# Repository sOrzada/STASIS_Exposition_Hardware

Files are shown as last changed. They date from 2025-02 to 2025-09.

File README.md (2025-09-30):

# STASIS_Exposure_Hardware
This is the repository for the exposure hardware of the STASIS project.
The corresponding software can be found in this repository: https://github.com/sOrzada/STASIS_Control

by Stephan Orzada @ German Cancer Research Center (DKFZ) 

# Overview
The STASIS RF exposure system is an open-source hardware and software platform designed for implant testing under exposure to radiofrequency (RF) fields, such as those encountered in the environment of an MRI system. For this purpose, the target RF frequency is 128 MHz, corresponding to the resonant frequency of protons in a 3 Tesla magnetic field. The system is capable of transmitting on eight independent RF channels, enabling parallel transmission.
To ensure the design is easily accessible to potential users, all design files and software are publicly available and can be accessed via the following repositories:
https://github.com/sOrzada/STASIS_Exposure_Hardware
https://github.com/sOrzada/STASIS_Control
All hardware components of the exposure system are licensed under the CERN-OHL-W while the software is licensed under a GNU GPL v3. In addition the project has been submitted to the conformity assessment body of the Open Source Imaging Initiative e.V. (https://www.opensourceimaging.org) to assess its open source status according to DIN SPEC 3105.  
To further improve accessibility, standard components with long production lifespans were selected wherever possible. For example, standard logic components were used instead of specialised microcontrollers or FPGAs.

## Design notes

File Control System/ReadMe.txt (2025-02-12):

This Folder contains the PCBs and Housings for the Control System of the STASIS project's RF exposition system.
The PCBs are provided in two different formats: Eagle and KiCAD.
The Housings-folder contains .step files for the housings and front panels of the Eurocards.

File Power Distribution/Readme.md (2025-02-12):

# Power Distribution
This folder contains the data for the power distribution of the STASIS RF exposition system.
The Power Distribution is provides a simple switch (and emergency switch) to switch the system's power on and off.
Furthermore, it switches each amplifier on 3s after the previous amplifier to prevent circuit breakers from acting.

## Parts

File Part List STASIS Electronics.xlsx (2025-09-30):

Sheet: Components Control System
Article | Description | URL | Amount | Unit Price | Subtotal | Distributor | Comment | Total
9031646921 | DIN41612 64P Typ C Male | 9031646921 (https://www.mouser.de/ProductDetail/HARTING/09031646921?qs=gIpPgrDBK%2Fgxgy%2FzqITWPQ%3D%3D) | 20 | 2.88 € | 57.60 € | Mouser | Modulators | 3439.22 €
9032646825 | DIN41612 64P Typ C Female | 9032646825 (https://www.mouser.de/ProductDetail/HARTING/09032646825?qs=gIpPgrDBK%2Fibxr4BbAh3hw%3D%3D) | 20 | 2.70 € | 54.00 € | Mouser
GCM188R71C104KA37J | 100nF 0603 | GCM188R71C104KA37J (https://www.mouser.de/ProductDetail/Murata-Electronics/GCM188R71C104KA37J?qs=sGAEpiMZZMvsSlwiRhF8qqDvUs8Zl92XYFoMhbKeCr4%3D) | 500 | 0.03 € | 13.50 € | Mouser
GRM1885C1H111GA01J | 110pF 0603 | GRM1885C1H111GA01J (https://www.mouser.de/ProductDetail/Murata-Electronics/GRM1885C1H111GA01J) | 30 | 0.11 € | 3.36 € | Mouser
C0603C271G2GACTU | 270pF 0603 | C0603C271G2GACTU (https://www.mouser.de/ProductDetail/KEMET/C0603C271G2GACTU) | 25 | 0.42 € | 10.50 € | Mouser
GCM1885C2A221JA16D | 220pF 0603 | GCM1885C2A221JA16D (https://www.mouser.de/ProductDetail/Murata-Electronics/GCM1885C2A221JA16D) | 25 | 0.07 € | 1.88 € | Mouser
EMF316AB7106KLHT | 10µF 1206 | EMF316AB7106KLHT (https://www.mouser.de/ProductDetail/Taiyo-Yuden/EMF316AB7106KLHT) | 50 | 0.21 € | 10.75 € | Mouser
GCM31CR70J226KE23L | 22µF 1206 | GCM31CR70J226KE23L (https://www.mouser.de/ProductDetail/Murata-Electronics/GCM31CR70J226KE23L) | 50 | 0.49 € | 24.45 € | Mouser
GRM1555C1E103JE01D | 10nF 0402 | GRM1555C1E103JE01D (https://www.mouser.de/ProductDetail/Murata-Electronics/GRM1555C1E103JE01D) | 50 | 0.08 € | 4.00 € | Mouser
08055A102KAT2A | 1nF 0805 | 08055A102KAT2A (https://www.mouser.de/ProductDetail/KYOCERA-AVX/08055A102KAT2A?qs=sGAEpiMZZMvsSlwiRhF8qsUJX4ZZq7O1iub2rREDztE%3D) | 100 | 0.16 € | 16.20 € | Mouser
GCM188R71H103KA37J | 10nF 0603 | GCM188R71H103KA37J (https://www.mouser.de/ProductDetail/Murata-Electronics/GCM188R71H103KA37J) | 500 | 0.02 € | 10.50 € | Mouser
BAT60BE6327HTSA1 | Schottky Diode SOD-323-2 | BAT60BE6327HTSA1 (https://www.mouser.de/ProductDetail/Infineon-Technologies/BAT60BE6327HTSA1?qs=K00xGehIljs1ioYh6e6mQw%3D%3D) | 30 | 0.41 € | 12.18 € | Mouser
SN74ALVC00NSR | Quad 2-Input Nand LVC SOIC-14 | https://www.mouser.de/ProductDetail/Texas-Instruments/SN74ALVC00NSR?qs=LfG3tU9ud8CLiczQYRPDsg%3D%3D | 10 | 0.44 € | 4.42 € | Mouser
SN74LVC04ANS | Hex Inverter LVC SOIC-14 | SN74LVC04ANS (https://www.mouser.de/ProductDetail/Texas-Instruments/SN74LVC04ANS?qs=4%2FQr8XCwynNuUCMn78xqww%3D%3D) | 10 | 0.99 € | 9.89 € | Mouser
SN74HC688DW | Comparator SO20W | SN74HC688DW (https://www.mouser.de/ProductDetail/Texas-Instruments/SN74HC688DW?qs=EIjG%252BN7kn%252BnsG9O57JMTyQ%3D%3D) | 50 | 1.36 € | 68.00 € | Mouser
SN74LVC1G17DCKR | Buffer single SC70-5 | SN74LVC1G17DCKR (https://www.mouser.de/ProductDetail/Texas-Instruments/SN74LVC1G17DCKR?qs=L5CvrNUdZioM7CGWSWVycQ%3D%3D) | 100 | 0.12 € | 12.00 € | Mouser
SN74LVC16373DLR | 16-bit Latch | SN74LVC16373DLR (https://www.mouser.de/ProductDetail/Texas-Instruments/SN74LVC16373DLR?qs=B7lSdIxWQklXUX7U1kIe%252BA%3D%3D) | 30 | 1.35 € | 40.50 € | Mouser
SN74LVC1G32DCKR | Single OR SC70-5 | SN74LVC1G32DCKR (https://www.mouser.de/ProductDetail/Texas-Instruments/SN74LVC1G32DCKR?qs=rshUhwi3fbYur8p35NB%252BLQ%3D%3D) | 100 | 0.16 € | 15.80 € | Mouser
SN74CB3Q16245DLR | 16bit bus switch ssop-48 | SN74CB3Q16245DLR (https://www.mouser.de/ProductDetail/Texas-Instruments/SN74CB3Q16245DLR?qs=ULgY8XwKjTnD7VhHoGZVNg%3D%3D) | 20 | 3.07 € | 61.40 € | Mouser
SN74LVCH16244ADLR | 16bit bus driver ssop-48 | SN74LVCH16244ADLR (https://www.mouser.de/ProductDetail/Texas-Instruments/SN74LVCH16244ADLR?qs=LfG3tU9ud8AVKX602AwiWw%3D%3D) | 40 | 1.41 € | 56.40 € | Mouser
SN74LVC1G04DCKR | Single Inverter SC70-5 | SN74LVC1G04DCKR (https://www.mouser.de/ProductDetail/Texas-Instruments/SN74LVC1G04DCKR?qs=dT9u2OTAaVWNPsQmeXyvkg%3D%3D) | 100 | 0.13 € | 13.40 € | Mouser
SN74LVC1G08DCKR | Single 2-Input AND SC70-5 | SN74LVC1G08DCKR (https://www.mouser.de/ProductDetail/Texas-Instruments/SN74LVC1G08DCKR?qs=sbcp%2F4gpy0%2F8FFQ%252BRQ5MTw%3D%3D) | 100 | 0.16 € | 16.40 € | Mouser
SN74LVC02ADRG4 | Quad 2-Input NOR | SN74LVC02ADRG4 (https://www.mouser.de/ProductDetail/Texas-Instruments/SN74LVC02ADRG4?qs=UG%2F8xqv%2F6WcgNHMmDPIwsw%3D%3D) | 18 | 0.39 € | 7.09 € | Mouser
10129381-904003BLF | Pin-Header 2x2 | 10129381-904003BLF (https://www.mouser.de/ProductDetail/Amphenol-FCI/10129381-904003BLF?qs=0lQeLiL1qyY7Xp84ndpsoA%3D%3D) | 16 | 0.10 € | 1.63 € | Mouser
77313-118-08LF | Pin-Header 2x4 | 77313-118-08LF (https://www.mouser.de/ProductDetail/Amphenol-FCI/77313-118-08LF?qs=xJiur%252Bgubk2jBBhypBJ8Ng%3D%3D) | 16 | 0.56 € | 8.96 € | Mouser
SX1100-B | Jumper | SX1100-B (https://www.mouser.de/ProductDetail/Kycon/SX1100-B?qs=oKK8NaWdAJvUJDIn2yWqug%3D%3D) | 100 | 0.04 € | 3.60 € | Mouser
0805AF-102XJRC | 1µH 0805 (2012) | 0805AF-102XJRC (https://www.mouser.de/ProductDetail/Coilcraft/0805AF-102XJRC?qs=JVZp5BaCFzh9pCHBndldQg%3D%3D) | 40 | 1.60 € | 64.00 € | Mouser
B82498F1152J | 1.5µH 0805 (2012) | B82498F1152J (https://www.mouser.de/ProductDetail/EPCOS-TDK/B82498F1152J?qs=iux7VCIsw52WrSZpCSeghA%3D%3D) | 40 | 0.58 € | 23.36 € | Mouser
WP710A10GD | 3mm LED Green | WP710A10GD (https://www.mouser.de/ProductDetail/Kingbright/WP710A10GD?qs=wRBQ8ZgBZ99oELJK8ikwDw%3D%3D) | 100 | 0.10 € | 10.00 € | Mouser
WP710A10ID | 3mm LED Red | WP710A10ID (https://www.mouser.de/ProductDetail/Kingbright/WP710A10ID?qs=wRBQ8ZgBZ98VyHeNIlWGkQ%3D%3D) | 100 | 0.10 € | 9.60 € | Mouser
RC0603FR-07100KL | 100kOhm 0603 | RC0603FR-07100KL (https://www.mouser.de/ProductDetail/YAGEO/RC0603FR-07100KL) | 500 | 0.01 € | 4.00 € | Mouser
RT0603BRE0750RL | 50Ohm 0603 | RT0603BRE0750RL (https://www.mouser.de/ProductDetail/YAGEO/RT0603BRE0750RL) | 100 | 0.11 € | 11.00 € | Mouser
ERJ-3EKF2001V | 2kOhm 0603 | ERJ-3EKF2001V (https://www.mouser.de/ProductDetail/Panasonic/ERJ-3EKF2001V?qs=sGAEpiMZZMvdGkrng054t8ugkoYZivkg3Db3Qcil2N0%3D) | 100 | 0.02 € | 2.00 € | Mouser
ERJ-3EKF2200V | 220Ohm 0603 | ERJ-3EKF2200V (https://www.mouser.de/ProductDetail/Panasonic/ERJ-3EKF2200V) | 100 | 0.02 € | 2.30 € | Mouser
ERJ-3GEY0R00V | 0Ohm 0603 | ERJ-3GEY0R00V (https://www.mouser.de/ProductDetail/Panasonic/ERJ-3GEY0R00V?qs=sGAEpiMZZMvdGkrng054t8ugkoYZivkg2RChYk5Dqt4%3D) | 100 | 0.02 € | 1.80 € | Mouser
ERJ-3EKF1001V | 1kOhm 0603 | ERJ-3EKF1001V (https://www.mouser.de/ProductDetail/Panasonic/ERJ-3EKF1001V?qs=sGAEpiMZZMvdGkrng054t8ugkoYZivkggtU4PdGL4Nk%3D) | 100 | 0.02 € | 2.00 € | Mouser
RC0603FR-07120RL | 120Ohm 0603 | RC0603FR-07120RL (https://www.mouser.de/ProductDetail/YAGEO/RC0603FR-07120RL) | 100 | 0.01 € | 0.70 € | Mouser
RC0603JR-13150RL | 150Ohm 0603 | RC0603JR-13150RL (https://www.mouser.de/ProductDetail/YAGEO/RC0603JR-13150RL) | 100 | 0.01 € | 0.90 € | Mouser
ADF08S04 | DIP switch 8 pos | ADF08S04 (https://www.mouser.de/ProductDetail/TE-Connectivity-Alcoswitch/ADF08S04?qs=SxaZfIVsCL01789ROZ7rzA%3D%3D) | 20 | 1.23 € | 24.60 € | Mouser
CY7C1021DV33-10ZSXIT | 64kx16 SRAM 10ns TSSOP-44II | CY7C1021DV33-10ZSXIT (https://www.mouser.de/ProductDetail/Infineon-Technologies/CY7C1021DV33-10ZSXIT?qs=PWZFpmwd5helP4DfKACbOQ%3D%3D) | 20 | 2.84 € | 56.80 € | Mouser
AD9754ARUZRL7 | 14-Bit ADC | AD9754ARUZRL7 (https://www.mouser.de/ProductDetail/Analog-Devices/AD9754ARUZRL7?qs=BpaRKvA4VqHe4d7qgcQcsg%3D%3D) | 20 | 24.95 € | 499.00 € | Mouser
DS1100LZ-20+ | 20ns Delay | DS1100LZ-20+ (https://www.mouser.de/ProductDetail/Maxim-Integrated/DS1100LZ-20%2b?qs=0Y9aZN%252BMVCV%2Fdv2VkDG0dA%3D%3D) | 10 | 8.09 € | 80.90 € | Mouser
ADL5385ACPZ-R7 | IQ-Modulator | ADL5385ACPZ-R7 (https://www.mouser.de/ProductDetail/Analog-Devices/ADL5385ACPZ-R7?qs=BpaRKvA4VqG4OwtCMETyCw%3D%3D) | 10 | 13.37 € | 133.70 € | Mouser
74LV393PW-Q100J | Counter IC | 74LV393PW-Q100J (https://www.mouser.de/ProductDetail/Nexperia/74LV393PW-Q100J?qs=fi7yB2oewZl1A%252BSGpgQ5jw%3D%3D) | 30 | 0.39 € | 11.64 € | Mouser
AZ1117IH-3.3TRG1 | LDO 3.3V | AZ1117IH-3.3TRG1 (https://www.mouser.de/ProductDetail/Diodes-Incorporated/AZ1117IH-3.3TRG1?qs=cpo3%2FpBou2jnS4SxLgAVoA%3D%3D) | 20 | 0.32 € | 6.42 € | Mouser
CONSMA002-L-G | SMA Con PCB-Panel | CONSMA002-L-G (https://www.mouser.de/ProductDetail/Linx-Technologies/CONSMA002-L-G?qs=vLWxofP3U2xfxfFnu8BdmA%3D%3D) | 50 | 5.81 € | 290.50 € | Mouser
710-860080375014 | 470µF 5mm | 860080375014 (https://www.mouser.de/ProductDetail/Wurth-Elektronik/860080375014?qs=0KOYDY2FL28YdH%252B8vgE2%252Bg%3D%3D) | 10 | 0.40 € | 4.00 € | Mouser | Power Supply
CR1206-FX-3300ELF | 330Ohm 1206 | CR1206-FX-3300ELF (https://www.mouser.de/ProductDetail/Bourns/CR1206-FX-3300ELF) | 100 | 0.02 € | 1.90 € | Mouser
HH18N102J500CT | 1nF 0603 | HH18N102J500CT (https://www.mouser.de/ProductDetail/Walsin/HH18N102J500CT) | 100 | 0.04 € | 3.50 € | Mouser | RF Splitter
B82498F3331J | 330nH 0805 | B82498F3331J (https://www.mouser.de/ProductDetail/EPCOS-TDK/B82498F3331J?qs=iux7VCIsw50bUV7hgS9AGw%3D%3D) | 10 | 0.48 € | 4.84 € | Mouser
TQP3M9008 | Broadband Amplifier | TQP3M9008 (https://www.mouser.de/ProductDetail/Qorvo/TQP3M9008?qs=ntQ%252BU8WgpwBNeAEBW36TMQ%3D%3D) | 5 | 6.07 € | 30.35 € | Mouser
GQM2195C2E180FB12D | 18pF 0805 RF capacitor | GQM2195C2E180FB12D (https://www.mouser.de/ProductDetail/Murata-Electronics/GQM2195C2E180FB12D?qs=sGAEpiMZZMvsSlwiRhF8qp0RtCwjIWiPtjVhVFjjz2I%3D) | 5 | 1.95 € | 9.75 € | Mouser | Signal Source
GQM2195C2E220JB12D | 22pF 0805 RF cap | GQM2195C2E220JB12D (https://www.mouser.de/ProductDetail/Murata-Electronics/GQM2195C2E220JB12D) | 5 | 0.92 € | 4.60 € | Mouser
GQM2195C2E330FB12D | 33pF 0805 RF cap | GQM2195C2E330FB12D (https://www.mouser.de/ProductDetail/Murata-Electronics/GQM2195C2E330FB12D) | 5 | 1.35 € | 6.75 € | Mouser
C1206C104J1RACAUTO | 100nF 1206 | C1206C104J1RACAUTO (https://www.mouser.de/ProductDetail/KEMET/C1206C104J1RACAUTO) | 100 | 0.11 € | 11.30 € | Mouser
SN74LVC1G02DCKR | Single 2-Input NOR SC70-5 | SN74LVC1G02DCKR (https://www.mouser.de/ProductDetail/Texas-Instruments/SN74LVC1G02DCKR?qs=HE9hdJajmerjAA9y3nGmcA%3D%3D) | 100 | 0.18 € | 17.60 € | Mouser
SN74LVC14ADRG3 | Hex Schmitt Inverter | SN74LVC14ADRG3 (https://www.mouser.de/ProductDetail/Texas-Instruments/SN74LVC14ADRG3?qs=C44r%252BX3hXgLOyR9T1KaQVg%3D%3D) | 5 | 0.54 € | 2.70 € | Mouser
AISC-1210-15NJ-T | 15nH 1210 | AISC-1210-15NJ-T (https://www.mouser.de/ProductDetail/ABRACON/AISC-1210-15NJ-T?qs=KpdAywxU010wlpUJrM445A%3D%3D) | 5 | 0.42 € | 2.10 € | Mouser
AISC-1210-R10J-T | 100nH 1210 | AISC-1210-R10J-T (https://www.mouser.de/ProductDetail/ABRACON/AISC-1210-R10J-T?qs=KpdAywxU011R3vUg8dJEpA%3D%3D) | 5 | 0.42 € | 2.10 € | Mouser
AISC-1210-82NJ-T | 82nH 1210 | AISC-1210-82NJ-T (https://www.mouser.de/ProductDetail/ABRACON/AISC-1210-82NJ-T?qs=KpdAywxU012iT2rq3hFlSg%3D%3D) | 5 | 0.35 € | 1.75 € | Mouser
AISC-1210-47NJ-T | 47nH 1210 | AISC-1210-47NJ-T (https://www.mouser.de/ProductDetail/ABRACON/AISC-1210-47NJ-T?qs=KpdAywxU010N9TqK2B9vCg%3D%3D) | 5 | 0.47 € | 2.35 € | Mouser
ERJ-6ENF1000V | 100Ohm 0805 | ERJ-6ENF1000V (https://www.mouser.de/ProductDetail/Panasonic/ERJ-6ENF1000V?qs=sGAEpiMZZMvdGkrng054t8ugkoYZivkgkz4QOj5IEgA%3D) | 100 | 0.02 € | 1.80 € | Mouser
RC0805FR-0768RL | 68 Ohm 0805 | RC0805FR-0768RL (https://www.mouser.de/ProductDetail/YAGEO/RC0805FR-0768RL?qs=sGAEpiMZZMvdGkrng054t8AJgcdMkx7x639rC03oyTs%3D) | 100 | 0.02 € | 1.70 € | Mouser
XLH538128.000000X | 128MHz CXO | XLH538128.000000X (https://www.mouser.de/ProductDetail/Renesas-Electronics/XLH538128.000000X?qs=itIaUkCn8qAeHGw2uhrs5w%3D%3D) | 5 | 2.38 € | 11.90 € | Mouser
MASWSS0115TR-3000 | RF switch SC70-6 | MASWSS0115TR-3000 (https://www.mouser.de/ProductDetail/MACOM/MASWSS0115TR-3000?qs=3Wmz%2FrCSAaEflvnPFG8Leg%3D%3D) | 10 | 1.42 € | 14.20 € | Mouser
SN74LV595ANSR | 8bit shift register | SN74LV595ANSR (https://www.mouser.de/ProductDetail/Texas-Instruments/SN74LV595ANSR?qs=UG%2F8xqv%2F6Wf1l209BjiXvA%3D%3D) | 10 | 1.07 € | 10.70 € | Mouser | SPI2Parallel
SN74LVC1G14DCKR | Single Schmitt Inverter | SN74LVC1G14DCKR (https://www.mouser.de/ProductDetail/Texas-Instruments/SN74LVC1G14DCKR?qs=j%2FZo4ajzVJKuhrRdLjfZIw%3D%3D) | 100 | 0.13 € | 12.80 € | Mouser
SN74LV393ANSR | Counter IC | SN74LV393ANSR (https://www.mouser.de/ProductDetail/Texas-Instruments/SN74LV393ANSR?qs=DcvZ7Fltd5w%252BshIxx2S2Bg%3D%3D) | 25 | 0.97 € | 24.27 € | Mouser
ERJ-3EKF1801V | 1.8kOhm 0603 | ERJ-3EKF1801V (https://www.mouser.de/ProductDetail/Panasonic/ERJ-3EKF1801V) | 100 | 0.02 € | 2.00 € | Mouser
CRCW0603220KFKEAC | 220KOhm 0603 | CRCW0603220KFKEAC (https://www.mouser.de/ProductDetail/Vishay-Dale/CRCW0603220KFKEAC) | 100 | 0.01 € | 0.80 € | Mouser
MM74HCT04MX | Hex Inverter HCT | MM74HCT04MX (https://www.mouser.de/ProductDetail/onsemi-Fairchild/MM74HCT04MX?qs=PYCkqoTEwR3wTRhpHjpTmg%3D%3D) | 3 | 0.69 € | 2.07 € | Mouser | UBL Splitter
ERJ-3GEYJ331V | 330Ohm 0603 | ERJ-3GEYJ331V (https://www.mouser.de/ProductDetail/Panasonic/ERJ-3GEYJ331V?qs=sGAEpiMZZMvdGkrng054t8ugkoYZivkgRPsbNS3nhOU%3D) | 100 | 0.02 € | 1.80 € | Mouser
ECS-TXO-2520MV-100-AN-TR | 10MHz TXO | ECS-TXO-2520MV-100-AN-TR (https://www.mouser.de/ProductDetail/ECS/ECS-TXO-2520MV-100-AN-TR?qs=bAKSY%2FctAC6D4eEwENGu8g%3D%3D) | 3 | 3.07 € | 9.21 € | Mouser | Timing Control
74LVC2G74DP,125 | D-Flip-Flop | 74LVC2G74DP,125 (https://www.mouser.de/ProductDetail/Nexperia/74LVC2G74DP125?qs=me8TqzrmIYX1iMHaYTXJug%3D%3D) | 5 | 0.51 € | 2.55 € | Mouser
UMFT4222EV-D | USB 2.0 to SPI Module | UMFT4222EV-D (https://www.mouser.de/ProductDetail/FTDI/UMFT4222EV-D?qs=F5EMLAvA7ICRJCgnkJGADg%3D%3D) | 2 | 20.63 € | 41.26 € | Mouser
BCS-112-L-S-TE | Sockel 12x1 | BCS-112-L-S-TE (https://www.mouser.de/ProductDetail/Samtec/BCS-112-L-S-TE?qs=92ilVni64gzptLUYzm9OlQ%3D%3D) | 4 | 3.32 € | 13.28 € | Mouser
77311-118-02LF | Pin Header 2x1 | 77311-118-02LF (https://www.mouser.de/ProductDetail/Amphenol-FCI/77311-118-02LF?qs=5xI8GKdkXlmD4cdGgiyi7w%3D%3D) | 4 | 0.24 € | 0.96 € | Mouser
AJ25HV | Trimmer 1-23pF 750V | AJ25HV (https://www.digikey.de/en/products/detail/knowles-voltronics/AJ25HV/7261406) | 20 | 48.89 € | 977.72 € | Digikey
SCA-4-10+ | 4-Way Splitter | SCA-4-10+ (https://www.minicircuits.com/WebStore/dashboard.html?model=SCA-4-10%2B) | 10 | 7.27 € | 72.70 € | Mini-Circuits
AKL 320-02 | Anschlussklemme 2-Pol Vert. | AKL 320-02 (https://www.reichelt.de/wannenstecker-fuer-akl-349-2-pol-rm5-0-akl-320-02-p36672.html?trstct=pos_9&nbc=1) | 5 | 0.33 € | 1.65 € | Reichelt
AKL 330-02 | Anschlussklemme 2-Pol Hor. | AKL 330-02 (https://www.reichelt.de/wannenstecker-fuer-akl-349-2-pol-rm5-0-akl-330-02-p36679.html?trstct=pos_5&nbc=1) | 5 | 0.35 € | 1.75 € | Reichelt
AKL 330-03 | Anschlussklemme 3-Pol Hor. | AKL 330-03 (https://www.reichelt.de/wannenstecker-fuer-akl-349-3-pol-rm5-0-akl-330-03-p36680.html?trstct=pos_9&nbc=1) | 5 | 0.53 € | 2.65 € | Reichelt
AKL 349-03 | Stecker 3-Pol | AKL 349-03 (https://www.reichelt.de/anschlussklemmensystem-3-pol-rm5-0-akl-349-03-p36666.html?trstct=pos_3&nbc=1) | 3 | 1.07 € | 3.21 € | Reichelt
AKL 349-02 | Stecker 2-Pol | AKL 349-02 (https://www.reichelt.de/anschlussklemmensystem-2-pol-rm5-0-akl-349-02-p36665.html?trstct=pos_4&nbc=1) | 3 | 0.72 € | 2.16 € | Reichelt
MW LRS-35-5 | Switching Power Supply 5V 7A | MW LRS-35-5 (https://www.reichelt.de/schaltnetzteil-geschlossen-35-w-5-v-7-a-mw-lrs-35-5-p202953.html) | 1 | 13.69 € | 13.69 € | Reichelt
KES 2SI | Einbaustecker + Sicherung | KES 2SI (https://www.reichelt.de/kaltgeraetestecker-mit-sicherungseinsatz-4-8-mm-faston-kes-2si-p9359.html?trstct=pol_7&nbc=1) | 10 | 1.99 € | 19.90 € | Reichelt
WIPPE 1855.1102 | Wippschalter rot beleuchtet | WIPPE 1855.1102 (https://www.reichelt.de/wippschalter-2x-aus-beleuchtet-rot-wippe-1855-1102-p36784.html?trstct=pol_1&nbc=1) | 10 | 4.35 € | 43.50 € | Reichelt
GC 2510-MB003 | USB A to Micro-C 30cm | GC 2510-MB003 (https://www.reichelt.de/usb-2-0-kabel-a-stecker-auf-micro-b-stecker-0-3-m-gc-2510-mb003-p202261.html?trstct=vrt_pdn&nbc=1) | 1 | 1.40 € | 1.40 € | Reichelt
CLIFF CP30207NM | USB Flange | CLIFF CP30207NM (https://www.reichelt.de/usb-adapter-ft-1-x-usb-2-0-b-buchse-1-x-usb-2-0-a-buchse-cliff-cp30207nm-p227651.html?trstct=pol_12&nbc=1) | 1 | 6.95 € | 6.95 € | Reichelt
 |  |  |  |  | 0.00 €
 |  |  |  |  | 0.00 €
SDT 21S | Drucktaster | https://www.reichelt.de/at/de/drucktaster-1a-120vac-1x-ein-gerade-loetfahnen-sdt-21s-p54297.html?trstct=pol_11&nbc=1 | 5 | 2.12 € | 10.60 € | Reichelt
KBT RTF-5020 | LED-Schirm | https://www.reichelt.de/at/de/led-halter-fuer-5-mm-leds-schwarz-kbt-rtf-5020-p232233.html?trstct=pol_1&nbc=1 | 5 | 0.22 € | 1.10 € | Reichelt
DI 5MM | Distanzhülsen 5mm M3 | https://www.reichelt.de/at/de/distanzhuelsen-metall-6-kant-m3-5mm-di-5mm-p7123.html?trstct=pos_2&nbc=1 | 100 | 0.13 € | 13.08 € | Reichelt
CR 88 Lötpaste | Lötpaste Bleifrei | https://www.reichelt.de/at/de/loetpaste-cr-88-no-clean-bleifrei-sn96-5ag3-5-10-gr-cr-88-p61392.html?trstct=pol_5&nbc=1 | 1 | 21.78 € | 21.78 € | Reichelt
Nachbestellungen:
74ALVC08D,118 | Quad AND Gate LVC | 74ALVC08D,118 (https://www.mouser.de/ProductDetail/Nexperia/74ALVC08D118?qs=P62ublwmbi%2F1DHq%252BMsm4ew%3D%3D) | 18 | 0.32 € | 5.71 € | Mouser
ADL5385ACPZ-R7 | IQ-Modulator | ADL5385ACPZ-R7 (https://www.mouser.de/ProductDetail/Analog-Devices/ADL5385ACPZ-R7?qs=BpaRKvA4VqG4OwtCMETyCw%3D%3D) | 5 | 13.37 € | 66.85 € | Mouser
 |  |  |  |  | 0.00 €
 |  |  |  |  | 0.00 €
AD8345AREZ-RL7 | I/Q-Modulator | AD8345AREZ-RL7 (https://www.mouser.de/ProductDetail/Analog-Devices/AD8345AREZ-RL7?qs=%2FtpEQrCGXCzXkfVgPpHsDQ%3D%3D) | 10 | 12.47 | 124.70 € | Mouser
ETC1-1-13TR | Transformer | https://www.mouser.de/ProductDetail/MACOM/ETC1-1-13TR?qs=3Wmz%2FrCSAaERPMP6steZ6g%3D%3D | 10 | 1.76 | 17.60 € | Mouser

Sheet: Components Body Coil
Article | Description | URL | Amount | Unit Price | Subtotal | Distributor | Comment | Total
23X36-1-1125 | Kupferfolie Selbstklebend | 23X36-1-1125 (https://www.digikey.de/de/products/detail/3m-tc/23X36-1-1125/3339655) | 4 | 50.74 € | 202.96 € | Digikey |  | 578.45 €
 |  |  |  |  | 0.00 €
1181 TAPE (1) | Kupferband, Selbstklebend Leitend | 1181 TAPE (1) (https://www.mouser.de/ProductDetail/3M-Electronic-Specialty/1181-TAPE-1?qs=fltJrqpyVmVSrCu3zSIrVQ%3D%3D) | 1 | 80.37 | 80.37 € | Mouser
 |  |  |  |  | 0.00 €
KNOPF 14-4 SW | Drehknopf 4mm ohne Deckel | https://www.reichelt.de/at/de/potentiometerknopf-fuer-achse-4-mm-schwarz-knopf-14-4-sw-p42072.html?trstct=pol_1&nbc=1 | 16 | 1.92 € | 30.72 € | Reichelt
DECKEL 14M SW | Kappe Schwarz | https://www.reichelt.de/at/de/abdeckkappe-fuer-knopf-14-knebel-20-6-25-6-schwarz-deckel-14m-sw-p42080.html?nbc=1&trstct=lsbght_sldr::42072 | 8 | 0.45 € | 3.60 € | Reichelt
DECKEL 14M RT | Kappe Rot | https://www.reichelt.de/at/de/abdeckkappe-fuer-knopf-14-knebel-20-6-25-6-rot-deckel-14m-rt-p42079.html?nbc=1&trstct=lsbght_sldr::42072 | 8 | 0.45 € | 3.60 € | Reichelt
VJ1111D330JXLAJ | 33pF 1111 630V RF | VJ1111D330JXLAJ (https://www.mouser.de/ProductDetail/Vishay-Vitramon/VJ1111D330JXLAJ) | 100 | 0.51 € | 51.00 € | Mouser | Body Array
VJ1111D200JXRAJ | 20pF 1111 1500V RF | VJ1111D200JXRAJ (https://www.mouser.de/ProductDetail/Vishay-Vitramon/VJ1111D200JXRAJ) | 10 | 1.24 € | 12.40 € | Mouser
VJ1111D180JXRAJ | 18pF 1111 1500V RF | VJ1111D180JXRAJ (https://www.mouser.de/ProductDetail/Vishay-Vitramon/VJ1111D180JXRAJ) | 25 | 1.24 € | 31.00 € | Mouser
VJ1111D561KXDAJ | 560pF 1111 300V RF | VJ1111D561KXDAJ (https://www.mouser.de/ProductDetail/Vishay-Vitramon/VJ1111D561KXDAJ) | 10 | 0.73 € | 7.30 € | Mouser
523-172170 | N Panel Mount SR141 | 523-172170 (https://www.mouser.de/ProductDetail/Amphenol-RF/172170?qs=VJoKNY%2FG7DYX%2F1HGX4%2FTeQ%3D%3D) | 8 | 12.86 € | 102.88 € | Mouser
SUCOFORM_141 | Semi-Flex Cable .141 | SUCOFORM_141 (https://www.mouser.de/ProductDetail/HUBER%2bSUHNER/SUCOFORM_141?qs=byeeYqUIh0Prk0bokjPpbA%3D%3D) | 6 | 8.77 € | 52.62 € | Mouser
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

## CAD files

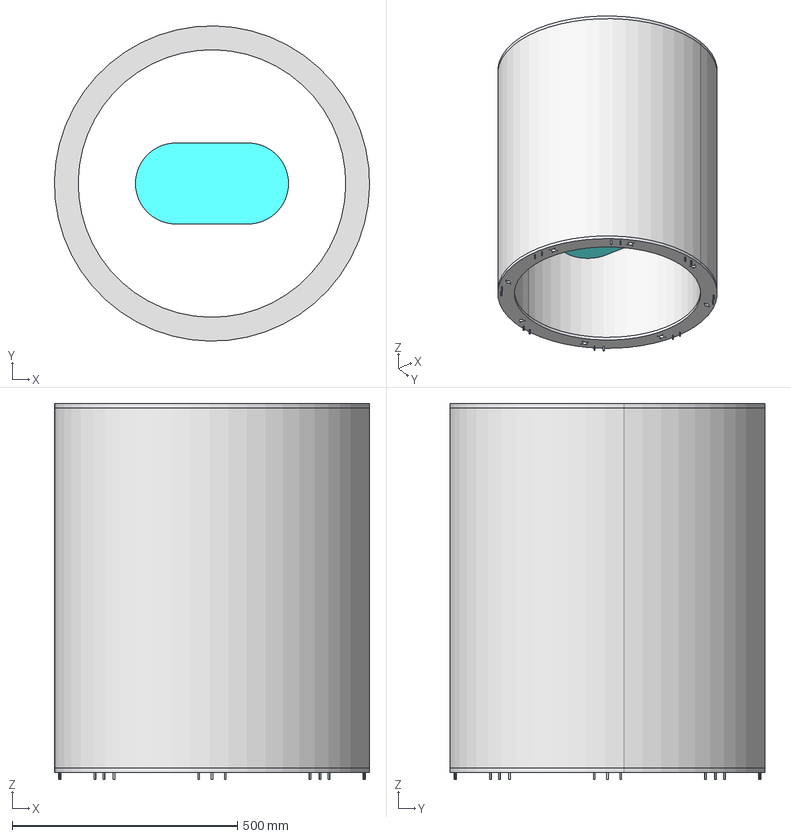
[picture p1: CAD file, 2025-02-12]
Array/Model_Coil_STASIS_Assembly.stp
699.9 x 699.9 x 835.0 mm
TEM conductor
Conductor End
Shield
PCB_Strip
PCB_end
PCB_end_1
PCB_end_2
PCB_end_3
PCB_end_4
PCB_end_5
PCB_end_6
PCB_end_7
PCB_end_8
PCB_end_9
PCB_end_10
PCB_end_11
PCB_end_12
PCB_end_13
PCB_end_14
PCB_end_15
PCB_Strip_1
PCB_Strip_2
PCB_Strip_3
PCB_Strip_4
PCB_Strip_5
PCB_Strip_6
PCB_Strip_7
Holders_Strip
Holders_Rod
Rods
Holders_Rod_1
Holders_Rod_2
Holders_Rod_3
Holders_Rod_4
Holders_Rod_5
Holders_Rod_6
Holders_Rod_7
Holders_Rod_8
Holders_Rod_9
Holders_Rod_10
Holders_Rod_11
Holders_Rod_12
Holders_Rod_13
Holders_Rod_14
Holders_Rod_15
Holders_Strip_1
Holders_Strip_2
Holders_Strip_3
Holders_Strip_4
Holders_Strip_5
Holders_Strip_6
Holders_Strip_7
Holders_Strip_8
Holders_Strip_9
Holders_Strip_10
Holders_Strip_11
Holders_Strip_12
Holders_Strip_13
Holders_Strip_14
Holders_Strip_15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

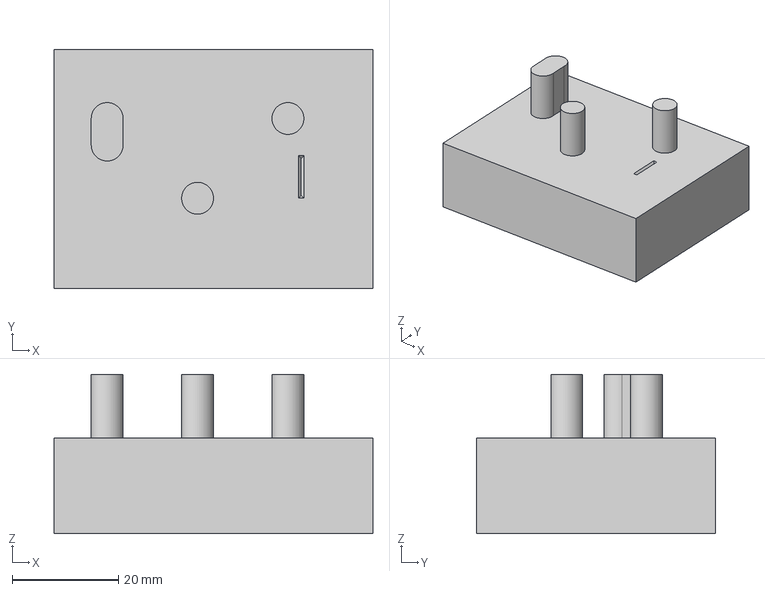
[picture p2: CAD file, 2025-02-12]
Amplifier/Bender_STASIS v3.step
60.0 x 45.0 x 30.0 mm

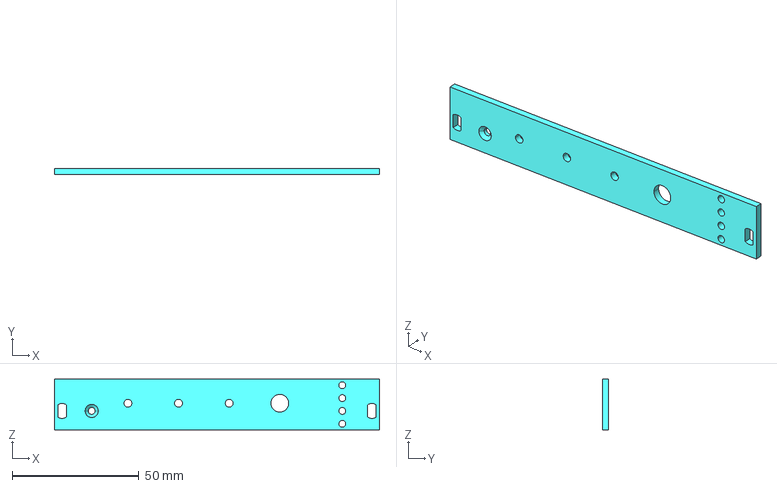
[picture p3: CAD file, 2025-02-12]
Control System/Housings/Frontplate_Timing_Control.stp
128.4 x 2.50 x 20.0 mm

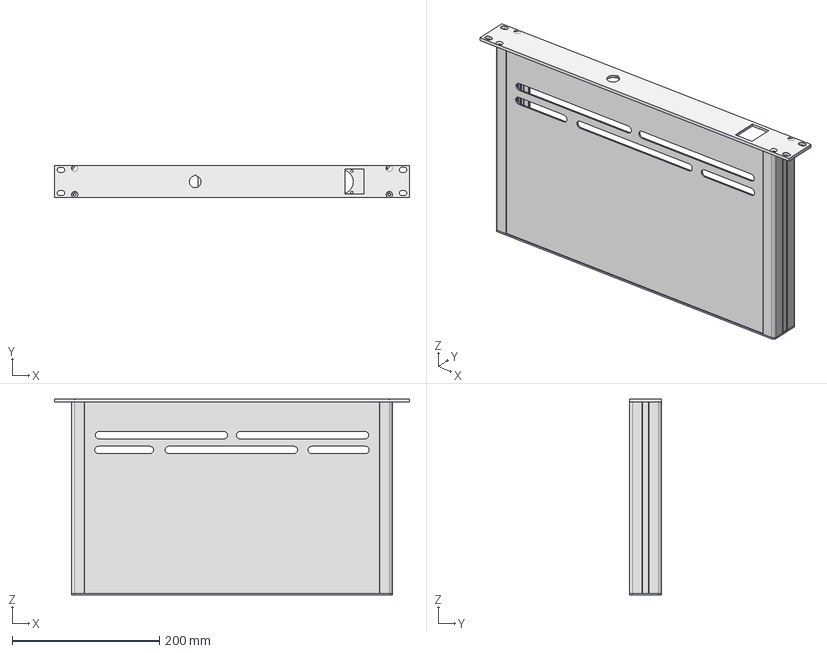
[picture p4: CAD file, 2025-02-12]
Power Distribution/Housing Power Distribution.step
482.6 x 43.7 x 266.0 mm
H0402F-E001F1E
SH-M3X8 x 2
H0403F-E001R1E

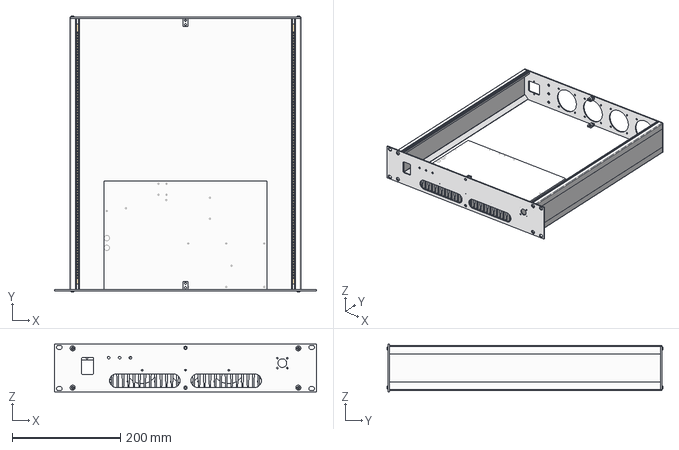
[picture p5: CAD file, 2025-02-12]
Amplifier/Amplifier Housing and Heatsink.step
483.0 x 508.2 x 88.1 mm

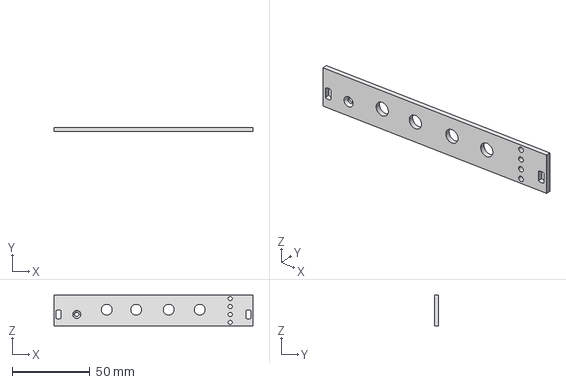
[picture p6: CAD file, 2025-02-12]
Control System/Housings/Frontplate_UBL.stp
128.4 x 2.50 x 20.0 mm

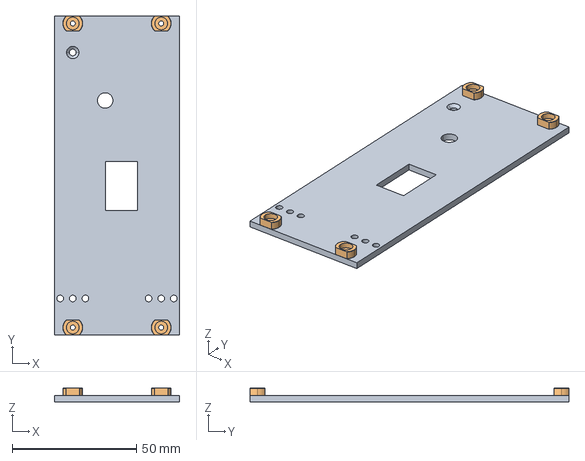
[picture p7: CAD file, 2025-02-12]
Control System/Housings/Frontplate_Power_Supply.stp
50.5 x 128.4 x 5.50 mm

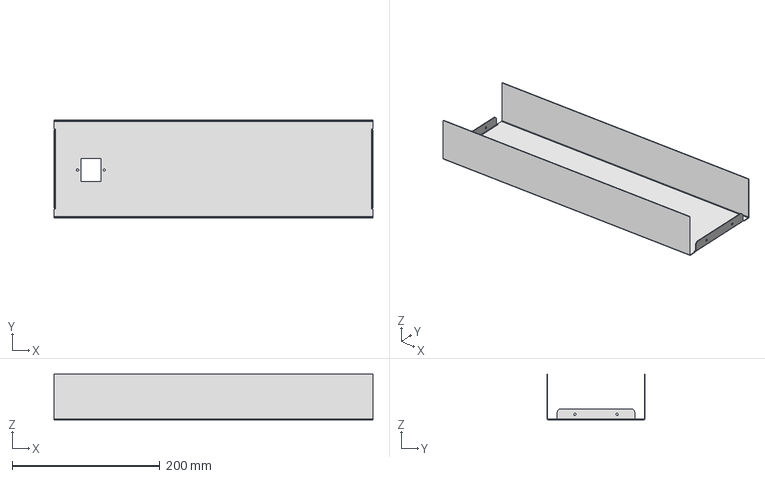
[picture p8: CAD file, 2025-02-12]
Control System/Housings/Backplate_Euro_Rack.stp
432.0 x 132.7 x 62.0 mm

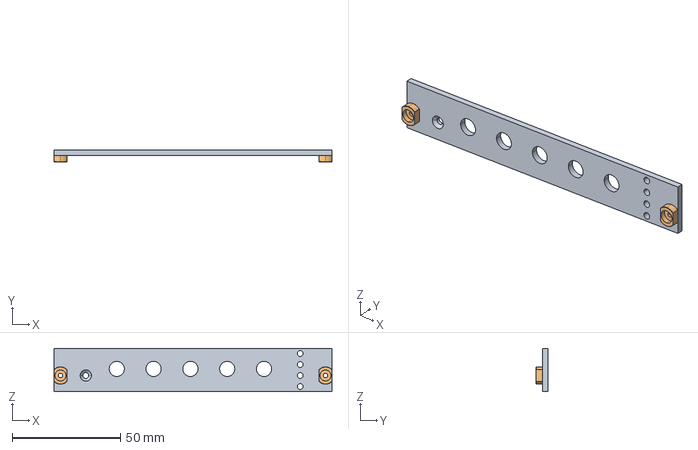
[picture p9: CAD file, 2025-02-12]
Control System/Housings/Frontplate_RF_Splitter.stp
128.4 x 5.50 x 20.0 mm

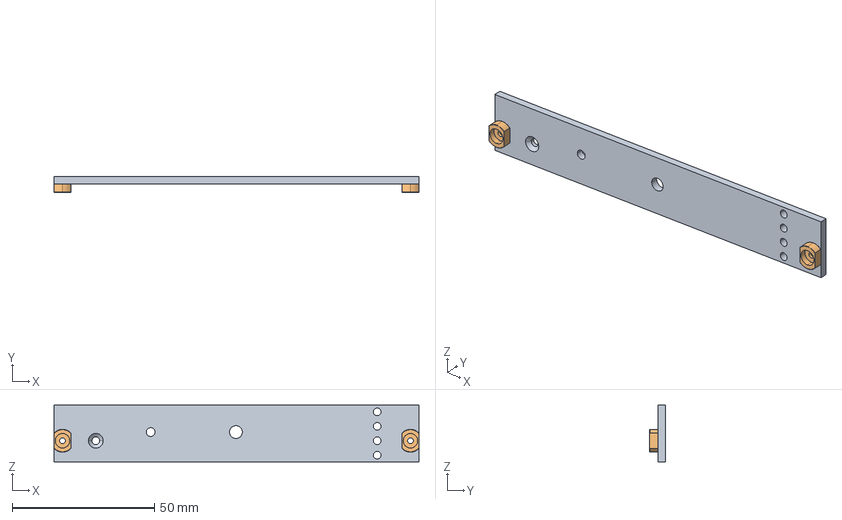
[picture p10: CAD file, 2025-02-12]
Control System/Housings/Frontplate_SPI2Parallel.stp
128.4 x 5.50 x 20.0 mm

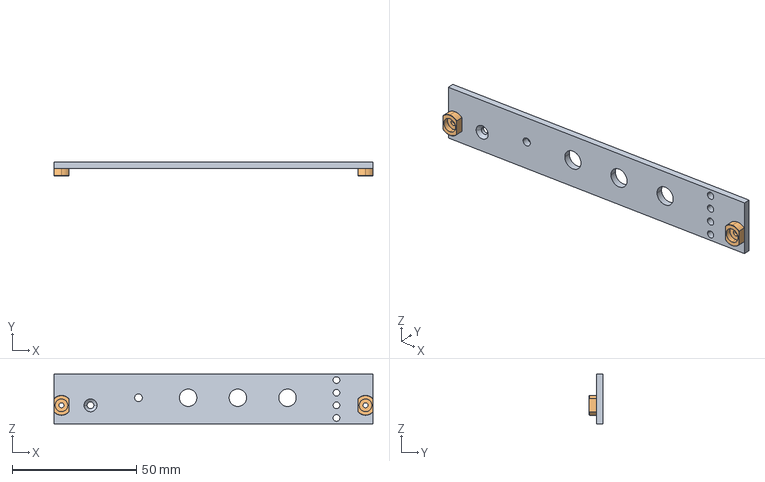
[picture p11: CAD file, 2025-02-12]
Control System/Housings/Frontplate_Modulator.stp
128.4 x 5.50 x 20.0 mm

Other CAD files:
Control System/Housings/Frontplate_USB2SPI.stp
Control System/Housings/Frontplate_RF_Gen.stp
Array/Coil housing 2 v2.f3d

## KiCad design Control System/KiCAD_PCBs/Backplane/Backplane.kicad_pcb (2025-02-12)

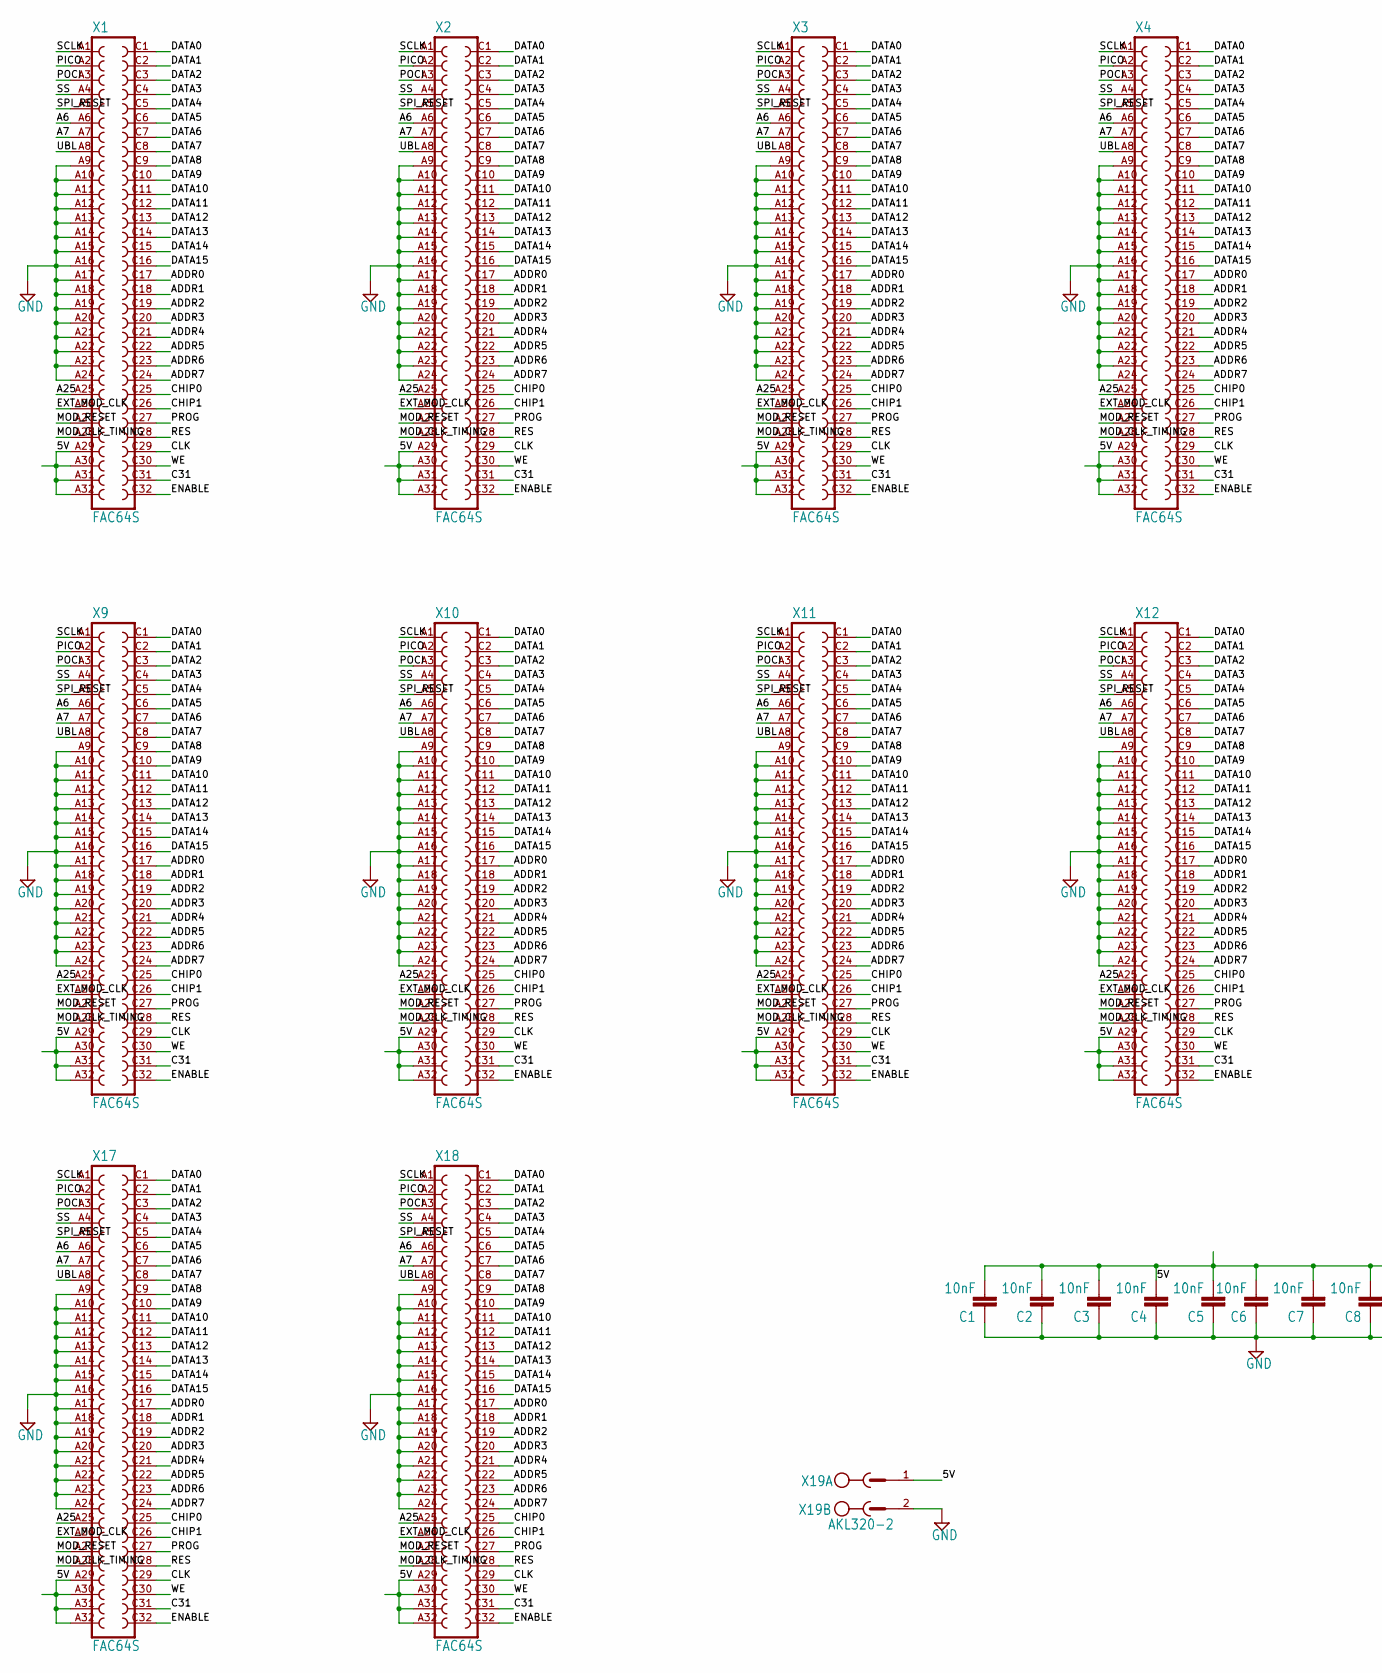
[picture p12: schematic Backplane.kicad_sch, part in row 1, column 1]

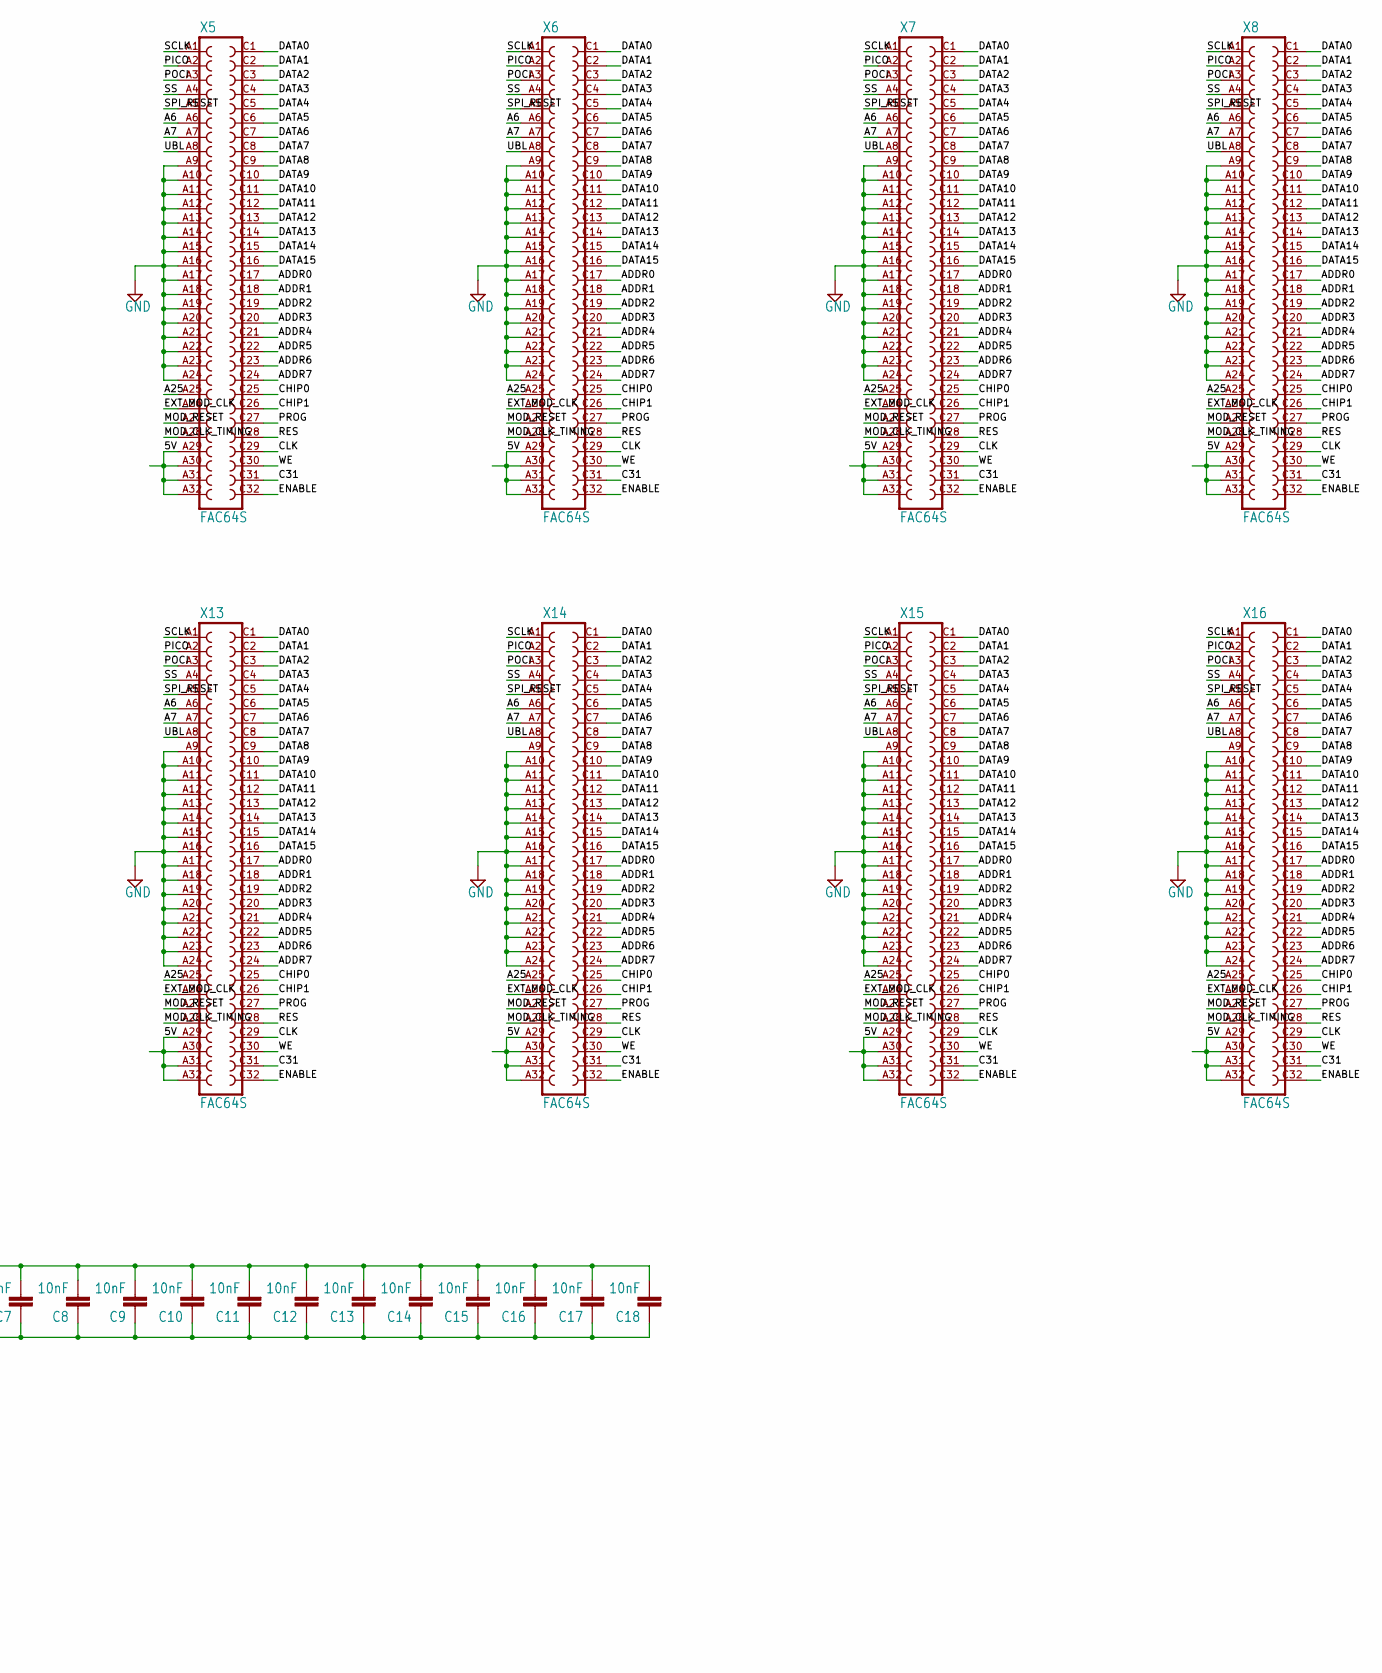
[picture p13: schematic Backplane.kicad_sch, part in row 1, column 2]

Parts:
C1, C2, C3, C4, C5, C6, C7, C8, C9, C10, C11, C12, C13, C14, C15, C16, C17, C18: 10nF; C0603
X1, X2, X3, X4, X5, X6, X7, X8, X9, X10, X11, X12, X13, X14, X15, X16, X17, X18: FAC64S
X19: AKL320-2; MSTBV2

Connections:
5V: C1.2, C2.2, C3.2, C4.2, C5.2, C6.2, C7.2, C8.2, C9.2, C10.2, C11.2, C12.2, C13.2, C14.2, C15.2, C16.2, C17.2, C18.2, X1.A29, X1.A30, X1.A31, X1.A32, X2.A29, X2.A30, X2.A31, X2.A32, X3.A29, X3.A30, X3.A31, X3.A32, X4.A29, X4.A30, X4.A31, X4.A32, X5.A29, X5.A30, X5.A31, X5.A32, X6.A29, X6.A30, X6.A31, X6.A32, X7.A29, X7.A30, X7.A31, X7.A32, X8.A29, X8.A30, X8.A31, X8.A32, X9.A29, X9.A30, X9.A31, X9.A32, X10.A29, X10.A30, X10.A31, X10.A32, X11.A29, X11.A30, X11.A31, X11.A32, X12.A29, X12.A30, X12.A31, X12.A32, X13.A29, X13.A30, X13.A31, X13.A32, X14.A29, X14.A30, X14.A31, X14.A32, X15.A29, X15.A30, X15.A31, X15.A32, X16.A29, X16.A30, X16.A31, X16.A32, X17.A29, X17.A30, X17.A31, X17.A32, X18.A29, X18.A30, X18.A31, X18.A32, X19.1
A6: X1.A6, X2.A6, X3.A6, X4.A6, X5.A6, X6.A6, X7.A6, X8.A6, X9.A6, X10.A6, X11.A6, X12.A6, X13.A6, X14.A6, X15.A6, X16.A6, X17.A6, X18.A6
A7: X1.A7, X2.A7, X3.A7, X4.A7, X5.A7, X6.A7, X7.A7, X8.A7, X9.A7, X10.A7, X11.A7, X12.A7, X13.A7, X14.A7, X15.A7, X16.A7, X17.A7, X18.A7
A25: X1.A25, X2.A25, X3.A25, X4.A25, X5.A25, X6.A25, X7.A25, X8.A25, X9.A25, X10.A25, X11.A25, X12.A25, X13.A25, X14.A25, X15.A25, X16.A25, X17.A25, X18.A25
ADDR0: X1.C17, X2.C17, X3.C17, X4.C17, X5.C17, X6.C17, X7.C17, X8.C17, X9.C17, X10.C17, X11.C17, X12.C17, X13.C17, X14.C17, X15.C17, X16.C17, X17.C17, X18.C17
ADDR1: X1.C18, X2.C18, X3.C18, X4.C18, X5.C18, X6.C18, X7.C18, X8.C18, X9.C18, X10.C18, X11.C18, X12.C18, X13.C18, X14.C18, X15.C18, X16.C18, X17.C18, X18.C18
ADDR2: X1.C19, X2.C19, X3.C19, X4.C19, X5.C19, X6.C19, X7.C19, X8.C19, X9.C19, X10.C19, X11.C19, X12.C19, X13.C19, X14.C19, X15.C19, X16.C19, X17.C19, X18.C19
ADDR3: X1.C20, X2.C20, X3.C20, X4.C20, X5.C20, X6.C20, X7.C20, X8.C20, X9.C20, X10.C20, X11.C20, X12.C20, X13.C20, X14.C20, X15.C20, X16.C20, X17.C20, X18.C20
ADDR4: X1.C21, X2.C21, X3.C21, X4.C21, X5.C21, X6.C21, X7.C21, X8.C21, X9.C21, X10.C21, X11.C21, X12.C21, X13.C21, X14.C21, X15.C21, X16.C21, X17.C21, X18.C21
ADDR5: X1.C22, X2.C22, X3.C22, X4.C22, X5.C22, X6.C22, X7.C22, X8.C22, X9.C22, X10.C22, X11.C22, X12.C22, X13.C22, X14.C22, X15.C22, X16.C22, X17.C22, X18.C22
ADDR6: X1.C23, X2.C23, X3.C23, X4.C23, X5.C23, X6.C23, X7.C23, X8.C23, X9.C23, X10.C23, X11.C23, X12.C23, X13.C23, X14.C23, X15.C23, X16.C23, X17.C23, X18.C23
ADDR7: X1.C24, X2.C24, X3.C24, X4.C24, X5.C24, X6.C24, X7.C24, X8.C24, X9.C24, X10.C24, X11.C24, X12.C24, X13.C24, X14.C24, X15.C24, X16.C24, X17.C24, X18.C24
C31: X1.C31, X2.C31, X3.C31, X4.C31, X5.C31, X6.C31, X7.C31, X8.C31, X9.C31, X10.C31, X11.C31, X12.C31, X13.C31, X14.C31, X15.C31, X16.C31, X17.C31, X18.C31
CHIP0: X1.C25, X2.C25, X3.C25, X4.C25, X5.C25, X6.C25, X7.C25, X8.C25, X9.C25, X10.C25, X11.C25, X12.C25, X13.C25, X14.C25, X15.C25, X16.C25, X17.C25, X18.C25
CHIP1: X1.C26, X2.C26, X3.C26, X4.C26, X5.C26, X6.C26, X7.C26, X8.C26, X9.C26, X10.C26, X11.C26, X12.C26, X13.C26, X14.C26, X15.C26, X16.C26, X17.C26, X18.C26
CLK: X1.C29, X2.C29, X3.C29, X4.C29, X5.C29, X6.C29, X7.C29, X8.C29, X9.C29, X10.C29, X11.C29, X12.C29, X13.C29, X14.C29, X15.C29, X16.C29, X17.C29, X18.C29
DATA0: X1.C1, X2.C1, X3.C1, X4.C1, X5.C1, X6.C1, X7.C1, X8.C1, X9.C1, X10.C1, X11.C1, X12.C1, X13.C1, X14.C1, X15.C1, X16.C1, X17.C1, X18.C1
DATA1: X1.C2, X2.C2, X3.C2, X4.C2, X5.C2, X6.C2, X7.C2, X8.C2, X9.C2, X10.C2, X11.C2, X12.C2, X13.C2, X14.C2, X15.C2, X16.C2, X17.C2, X18.C2
DATA2: X1.C3, X2.C3, X3.C3, X4.C3, X5.C3, X6.C3, X7.C3, X8.C3, X9.C3, X10.C3, X11.C3, X12.C3, X13.C3, X14.C3, X15.C3, X16.C3, X17.C3, X18.C3
DATA3: X1.C4, X2.C4, X3.C4, X4.C4, X5.C4, X6.C4, X7.C4, X8.C4, X9.C4, X10.C4, X11.C4, X12.C4, X13.C4, X14.C4, X15.C4, X16.C4, X17.C4, X18.C4
DATA4: X1.C5, X2.C5, X3.C5, X4.C5, X5.C5, X6.C5, X7.C5, X8.C5, X9.C5, X10.C5, X11.C5, X12.C5, X13.C5, X14.C5, X15.C5, X16.C5, X17.C5, X18.C5
DATA5: X1.C6, X2.C6, X3.C6, X4.C6, X5.C6, X6.C6, X7.C6, X8.C6, X9.C6, X10.C6, X11.C6, X12.C6, X13.C6, X14.C6, X15.C6, X16.C6, X17.C6, X18.C6
DATA6: X1.C7, X2.C7, X3.C7, X4.C7, X5.C7, X6.C7, X7.C7, X8.C7, X9.C7, X10.C7, X11.C7, X12.C7, X13.C7, X14.C7, X15.C7, X16.C7, X17.C7, X18.C7
DATA7: X1.C8, X2.C8, X3.C8, X4.C8, X5.C8, X6.C8, X7.C8, X8.C8, X9.C8, X10.C8, X11.C8, X12.C8, X13.C8, X14.C8, X15.C8, X16.C8, X17.C8, X18.C8
DATA8: X1.C9, X2.C9, X3.C9, X4.C9, X5.C9, X6.C9, X7.C9, X8.C9, X9.C9, X10.C9, X11.C9, X12.C9, X13.C9, X14.C9, X15.C9, X16.C9, X17.C9, X18.C9
DATA9: X1.C10, X2.C10, X3.C10, X4.C10, X5.C10, X6.C10, X7.C10, X8.C10, X9.C10, X10.C10, X11.C10, X12.C10, X13.C10, X14.C10, X15.C10, X16.C10, X17.C10, X18.C10
DATA10: X1.C11, X2.C11, X3.C11, X4.C11, X5.C11, X6.C11, X7.C11, X8.C11, X9.C11, X10.C11, X11.C11, X12.C11, X13.C11, X14.C11, X15.C11, X16.C11, X17.C11, X18.C11
DATA11: X1.C12, X2.C12, X3.C12, X4.C12, X5.C12, X6.C12, X7.C12, X8.C12, X9.C12, X10.C12, X11.C12, X12.C12, X13.C12, X14.C12, X15.C12, X16.C12, X17.C12, X18.C12
DATA12: X1.C13, X2.C13, X3.C13, X4.C13, X5.C13, X6.C13, X7.C13, X8.C13, X9.C13, X10.C13, X11.C13, X12.C13, X13.C13, X14.C13, X15.C13, X16.C13, X17.C13, X18.C13
DATA13: X1.C14, X2.C14, X3.C14, X4.C14, X5.C14, X6.C14, X7.C14, X8.C14, X9.C14, X10.C14, X11.C14, X12.C14, X13.C14, X14.C14, X15.C14, X16.C14, X17.C14, X18.C14
DATA14: X1.C15, X2.C15, X3.C15, X4.C15, X5.C15, X6.C15, X7.C15, X8.C15, X9.C15, X10.C15, X11.C15, X12.C15, X13.C15, X14.C15, X15.C15, X16.C15, X17.C15, X18.C15
DATA15: X1.C16, X2.C16, X3.C16, X4.C16, X5.C16, X6.C16, X7.C16, X8.C16, X9.C16, X10.C16, X11.C16, X12.C16, X13.C16, X14.C16, X15.C16, X16.C16, X17.C16, X18.C16
ENABLE: X1.C32, X2.C32, X3.C32, X4.C32, X5.C32, X6.C32, X7.C32, X8.C32, X9.C32, X10.C32, X11.C32, X12.C32, X13.C32, X14.C32, X15.C32, X16.C32, X17.C32, X18.C32
EXT_MOD_CLK: X1.A26, X2.A26, X3.A26, X4.A26, X5.A26, X6.A26, X7.A26, X8.A26, X9.A26, X10.A26, X11.A26, X12.A26, X13.A26, X14.A26, X15.A26, X16.A26, X17.A26, X18.A26
GND: C1.1, C2.1, C3.1, C4.1, C5.1, C6.1, C7.1, C8.1, C9.1, C10.1, C11.1, C12.1, C13.1, C14.1, C15.1, C16.1, C17.1, C18.1, X1.A9, X1.A10, X1.A11, X1.A12, X1.A13, X1.A14, X1.A15, X1.A16, X1.A17, X1.A18, X1.A19, X1.A20, X1.A21, X1.A22, X1.A23, X1.A24, X2.A9, X2.A10, X2.A11, X2.A12, X2.A13, X2.A14, X2.A15, X2.A16, X2.A17, X2.A18, X2.A19, X2.A20, X2.A21, X2.A22, X2.A23, X2.A24, X3.A9, X3.A10, X3.A11, X3.A12, X3.A13, X3.A14, X3.A15, X3.A16, X3.A17, X3.A18, X3.A19, X3.A20, X3.A21, X3.A22, X3.A23, X3.A24, X4.A9, X4.A10, X4.A11, X4.A12, X4.A13, X4.A14, X4.A15, X4.A16, X4.A17, X4.A18, X4.A19, X4.A20, X4.A21, X4.A22, X4.A23, X4.A24, X5.A9, X5.A10, X5.A11, X5.A12, X5.A13, X5.A14, X5.A15, X5.A16, X5.A17, X5.A18, X5.A19, X5.A20, X5.A21, X5.A22, X5.A23, X5.A24, X6.A9, X6.A10, X6.A11, X6.A12, X6.A13, X6.A14, X6.A15, X6.A16, X6.A17, X6.A18, X6.A19, X6.A20, X6.A21, X6.A22, X6.A23, X6.A24, X7.A9, X7.A10, X7.A11, X7.A12, X7.A13, X7.A14, X7.A15, X7.A16, X7.A17, X7.A18, X7.A19, X7.A20, X7.A21, X7.A22, X7.A23, X7.A24, X8.A9, X8.A10, X8.A11, X8.A12, X8.A13, X8.A14, X8.A15, X8.A16, X8.A17, X8.A18, X8.A19, X8.A20, X8.A21, X8.A22, X8.A23, X8.A24, X9.A9, X9.A10, X9.A11, X9.A12, X9.A13, X9.A14, X9.A15, X9.A16, X9.A17, X9.A18, X9.A19, X9.A20, X9.A21, X9.A22, X9.A23, X9.A24, X10.A9, X10.A10, X10.A11, X10.A12, X10.A13, X10.A14, X10.A15, X10.A16, X10.A17, X10.A18, X10.A19, X10.A20, X10.A21, X10.A22, X10.A23, X10.A24, X11.A9, X11.A10, X11.A11, X11.A12, X11.A13, X11.A14, X11.A15, X11.A16, X11.A17, X11.A18, X11.A19, X11.A20, X11.A21, X11.A22, X11.A23, X11.A24, X12.A9, X12.A10, X12.A11, X12.A12, X12.A13, X12.A14, X12.A15, X12.A16, X12.A17, X12.A18, X12.A19, X12.A20, X12.A21, X12.A22, X12.A23, X12.A24, X13.A9, X13.A10, X13.A11, X13.A12, X13.A13, X13.A14, X13.A15, X13.A16, X13.A17, X13.A18, X13.A19, X13.A20, X13.A21, X13.A22, X13.A23, X13.A24, X14.A9, X14.A10, X14.A11, X14.A12, X14.A13, X14.A14, X14.A15, X14.A16, X14.A17, X14.A18, X14.A19, X14.A20, X14.A21, X14.A22, X14.A23, X14.A24, X15.A9, X15.A10, X15.A11, X15.A12, X15.A13, X15.A14, X15.A15, X15.A16, X15.A17, X15.A18, X15.A19, X15.A20, X15.A21, X15.A22, X15.A23, X15.A24, X16.A9, X16.A10, X16.A11, X16.A12, X16.A13, X16.A14, X16.A15, X16.A16, X16.A17, X16.A18, X16.A19, X16.A20, X16.A21, X16.A22, X16.A23, X16.A24, X17.A9, X17.A10, X17.A11, X17.A12, X17.A13, X17.A14, X17.A15, X17.A16, X17.A17, X17.A18, X17.A19, X17.A20, X17.A21, X17.A22, X17.A23, X17.A24, X18.A9, X18.A10, X18.A11, X18.A12, X18.A13, X18.A14, X18.A15, X18.A16, X18.A17, X18.A18, X18.A19, X18.A20, X18.A21, X18.A22, X18.A23, X18.A24, X19.2
MOD_CLK_TIMING: X1.A28, X2.A28, X3.A28, X4.A28, X5.A28, X6.A28, X7.A28, X8.A28, X9.A28, X10.A28, X11.A28, X12.A28, X13.A28, X14.A28, X15.A28, X16.A28, X17.A28, X18.A28
MOD_RESET: X1.A27, X2.A27, X3.A27, X4.A27, X5.A27, X6.A27, X7.A27, X8.A27, X9.A27, X10.A27, X11.A27, X12.A27, X13.A27, X14.A27, X15.A27, X16.A27, X17.A27, X18.A27
PICO: X1.A2, X2.A2, X3.A2, X4.A2, X5.A2, X6.A2, X7.A2, X8.A2, X9.A2, X10.A2, X11.A2, X12.A2, X13.A2, X14.A2, X15.A2, X16.A2, X17.A2, X18.A2
POCI: X1.A3, X2.A3, X3.A3, X4.A3, X5.A3, X6.A3, X7.A3, X8.A3, X9.A3, X10.A3, X11.A3, X12.A3, X13.A3, X14.A3, X15.A3, X16.A3, X17.A3, X18.A3
PROG: X1.C27, X2.C27, X3.C27, X4.C27, X5.C27, X6.C27, X7.C27, X8.C27, X9.C27, X10.C27, X11.C27, X12.C27, X13.C27, X14.C27, X15.C27, X16.C27, X17.C27, X18.C27
RES: X1.C28, X2.C28, X3.C28, X4.C28, X5.C28, X6.C28, X7.C28, X8.C28, X9.C28, X10.C28, X11.C28, X12.C28, X13.C28, X14.C28, X15.C28, X16.C28, X17.C28, X18.C28
SCLK: X1.A1, X2.A1, X3.A1, X4.A1, X5.A1, X6.A1, X7.A1, X8.A1, X9.A1, X10.A1, X11.A1, X12.A1, X13.A1, X14.A1, X15.A1, X16.A1, X17.A1, X18.A1
SPI_RESET: X1.A5, X2.A5, X3.A5, X4.A5, X5.A5, X6.A5, X7.A5, X8.A5, X9.A5, X10.A5, X11.A5, X12.A5, X13.A5, X14.A5, X15.A5, X16.A5, X17.A5, X18.A5
SS: X1.A4, X2.A4, X3.A4, X4.A4, X5.A4, X6.A4, X7.A4, X8.A4, X9.A4, X10.A4, X11.A4, X12.A4, X13.A4, X14.A4, X15.A4, X16.A4, X17.A4, X18.A4
UBL: X1.A8, X2.A8, X3.A8, X4.A8, X5.A8, X6.A8, X7.A8, X8.A8, X9.A8, X10.A8, X11.A8, X12.A8, X13.A8, X14.A8, X15.A8, X16.A8, X17.A8, X18.A8
WE: X1.C30, X2.C30, X3.C30, X4.C30, X5.C30, X6.C30, X7.C30, X8.C30, X9.C30, X10.C30, X11.C30, X12.C30, X13.C30, X14.C30, X15.C30, X16.C30, X17.C30, X18.C30

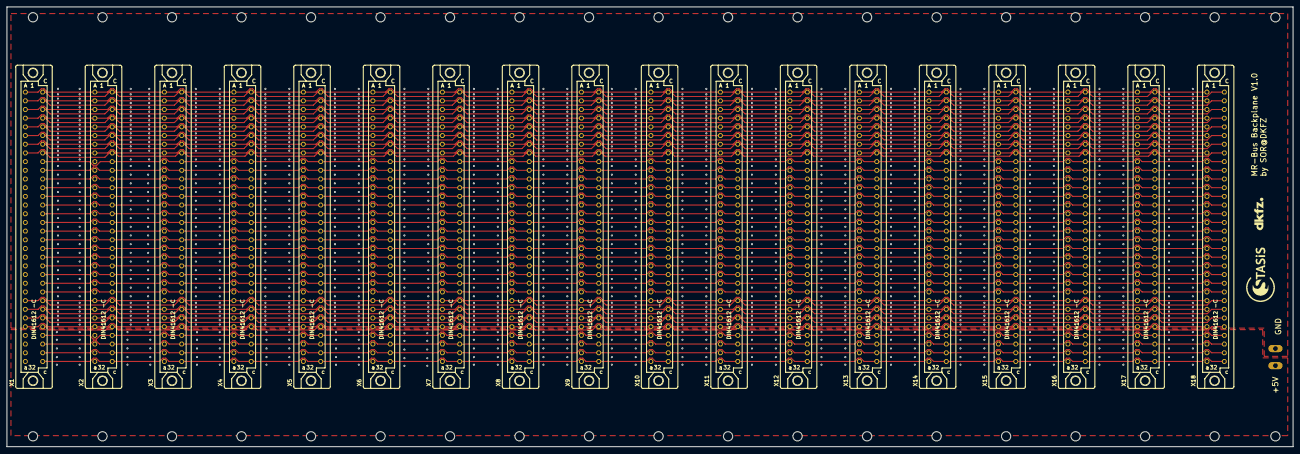
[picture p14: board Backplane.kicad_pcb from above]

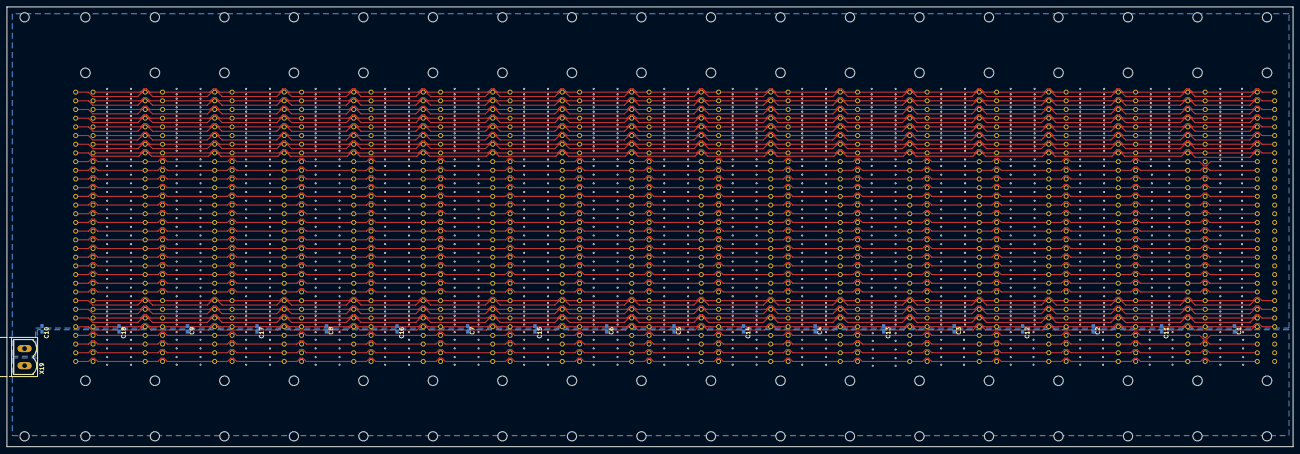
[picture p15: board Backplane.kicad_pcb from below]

Board: 2 copper layers, 376.0 x 128.6 mm, 77 parts (19 on the bottom side), 46 nets.

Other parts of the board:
@HOLE0, @HOLE1, @HOLE2, @HOLE3, @HOLE4, @HOLE5, @HOLE6, @HOLE7, @HOLE8, @HOLE9, @HOLE10, @HOLE11, @HOLE12, @HOLE13, @HOLE14, @HOLE15, @HOLE16, @HOLE17, @HOLE18, @HOLE19, @HOLE20, @HOLE21, @HOLE22, @HOLE23, @HOLE24, @HOLE25, @HOLE26, @HOLE27, @HOLE28, @HOLE29, @HOLE30, @HOLE31, @HOLE32, @HOLE33, @HOLE34, @HOLE35, @HOLE36, @HOLE37: (no value)
U$1: LOGO_STASIS
U$2: LOGO_DKFZ

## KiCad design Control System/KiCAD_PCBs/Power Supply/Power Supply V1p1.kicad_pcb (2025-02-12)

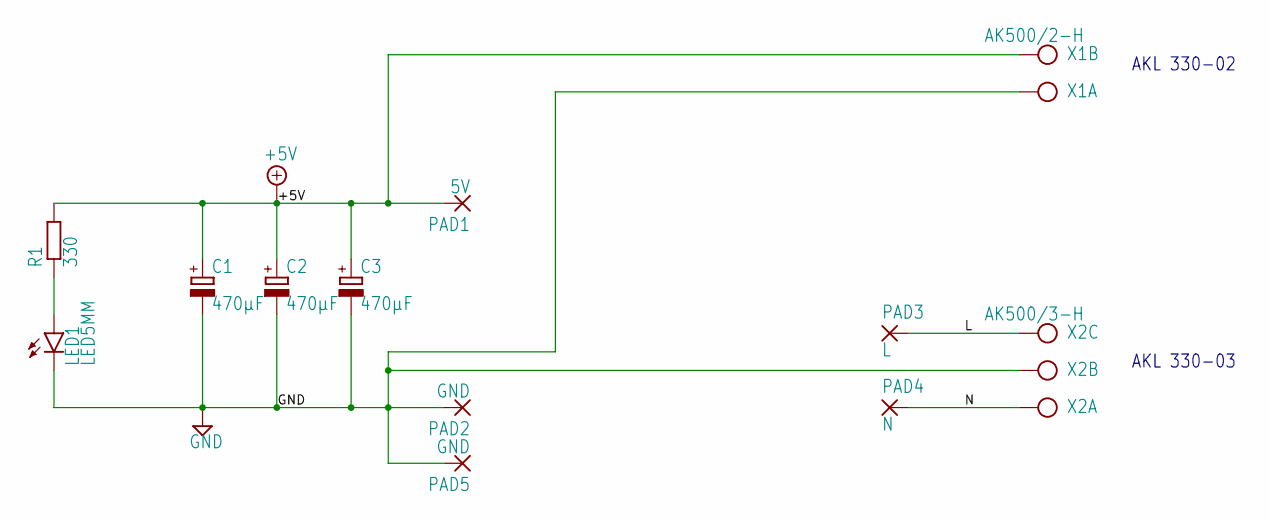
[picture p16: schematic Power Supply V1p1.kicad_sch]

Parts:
C1, C2, C3: 470µF; E5-10,5
LED1: LED5MM
PAD1: 5V; SMD2,54-5,08
PAD2, PAD5: GND; SMD2,54-5,08
PAD3: L; SMD2,54-5,08
PAD4: N; SMD2,54-5,08
R1: 330; R1206
X1: AK500/2-H; AK500_2-H
X2: AK500/3-H; AK500_3-H

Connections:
+5V: C1.+, C2.+, C3.+, PAD1.1, R1.2, X1.2
GND: C1.-, C2.-, C3.-, LED1.K (C), PAD2.1, PAD5.1, X1.1, X2.2
L: PAD3.1, X2.3
N: PAD4.1, X2.1
unnamed: LED1.A, R1.1

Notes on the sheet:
AKL 330-02
AKL 330-03

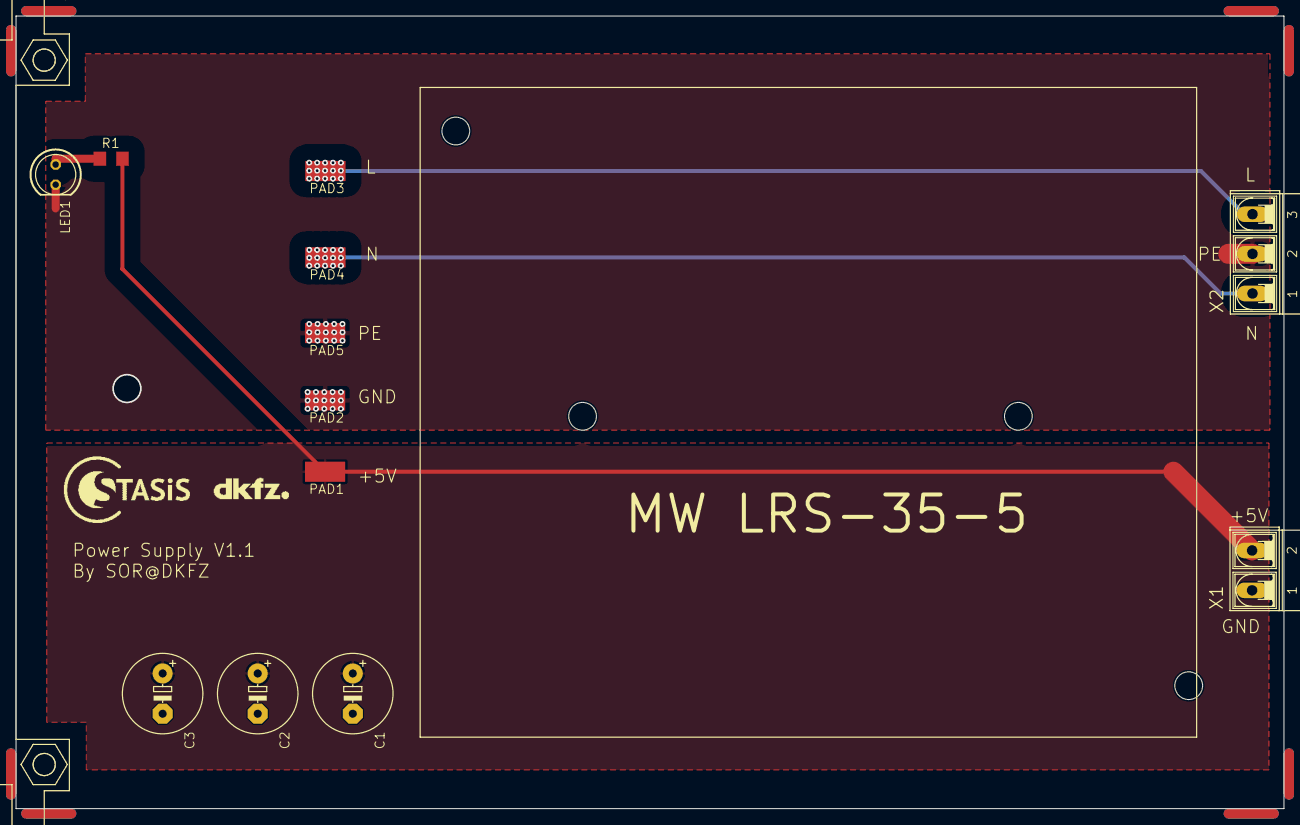
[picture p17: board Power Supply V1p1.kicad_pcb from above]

Board: 2 copper layers, 160.0 x 100.0 mm, 19 parts (0 on the bottom side), 5 nets.

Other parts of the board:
@HOLE0, @HOLE1, @HOLE2, @HOLE3: (no value)
U$1: EK-FP_79
U$2: LOGO_STASIS
U$3: LOGO_DKFZ

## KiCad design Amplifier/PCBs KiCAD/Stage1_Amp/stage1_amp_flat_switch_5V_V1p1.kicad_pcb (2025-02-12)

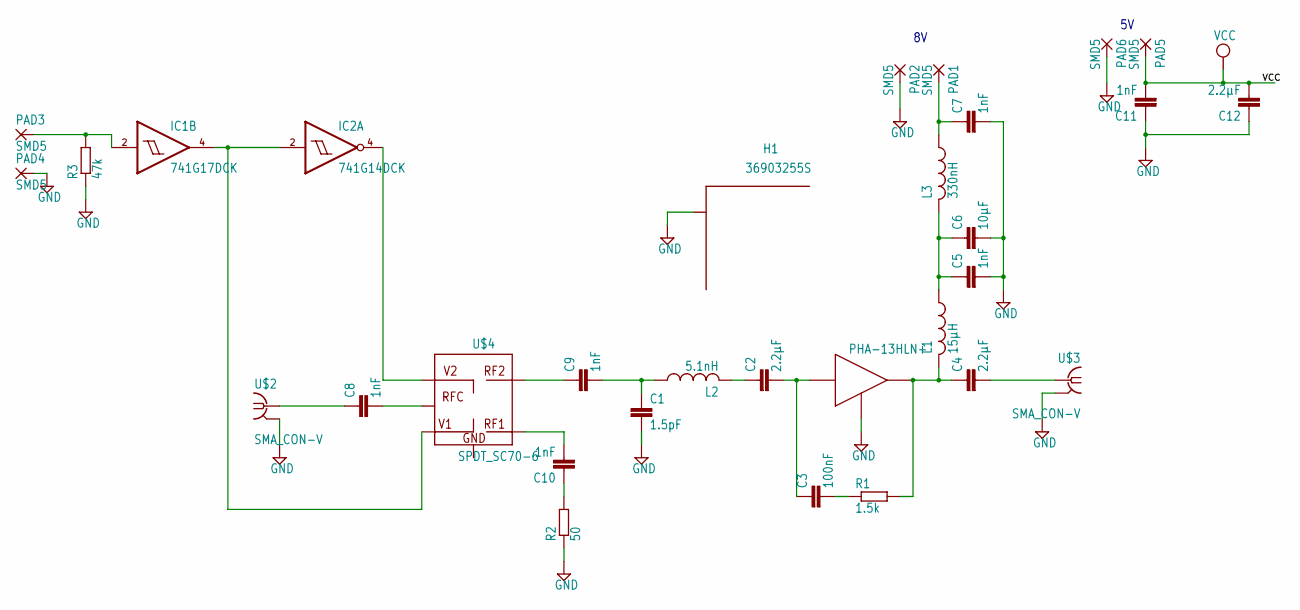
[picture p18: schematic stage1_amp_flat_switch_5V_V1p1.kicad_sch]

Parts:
C1: 1.5pF; C0402
C2, C4, C12: 2.2µF; C0402
C3: 100nF; C0402
C5, C7, C8, C9, C10, C11: 1nF; C0402
C6: 10µF; C0805
H1: 36903255S; WE-SHC_ONE-PIECE_36903255S
IC1: 741G17DCK; SC70-5
IC2: 741G14DCK; SC70-5
L1: 15µH; L3225M
L2: 5.1nH; L2012C
L3: 330nH; L3225M
PAD1, PAD2, PAD3, PAD4, PAD5, PAD6: SMD5; SMD2,54-5,08
R1: 1.5k; R0402
R2: 50; R0402
R3: 47k; R0805
U$1: PHA-13HLN+; SOT89
U$2, U$3: SMA_CON-V; BU-SMA-V
U$4: SPDT_SC70-6; SC70-6

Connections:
GND: C1.2, C5.2, C6.2, C7.2, C11.1, C12.1, H1.1, H1.2, H1.3, H1.4, H1.5, H1.6, H1.7, H1.8, H1.9, H1.10, H1.11, H1.12, H1.13, H1.14, H1.15, H1.16, H1.17, H1.18, H1.19, H1.20, IC1.3 (GND), IC2.3 (GND), PAD2.1, PAD4.1, PAD6.1, R2.1, R3.1, U$1.2 (GND), U$1.2@1 (GND), U$2.2 (GND@1), U$2.3 (GND@1), U$2.4 (GND@1), U$2.5 (GND@1), U$3.2 (GND@1), U$3.3 (GND@1), U$3.4 (GND@1), U$3.5 (GND@1)
unnamed: C2.1, L2.2
unnamed: C2.2, C3.1, U$1.1 (IN)
unnamed: C4.1, L1.2, R1.2, U$1.3 (OUT)
unnamed: C1.1, C9.2, L2.1
unnamed: C3.2, R1.1
unnamed: C4.2, U$3.1
unnamed: C5.1, C6.1, L1.1, L3.2
unnamed: C7.1, L3.1, PAD1.1
unnamed: C8.2, U$4.5 (RFC)
unnamed: C8.1, U$2.1
unnamed: C9.1, U$4.3 (RF2)
unnamed: C10.2, U$4.1 (RF1)
unnamed: C10.1, R2.2
unnamed: IC1.4 (O), IC2.2 (I), U$4.6 (V1)
unnamed: IC2.4 (O), U$4.4 (V2)
unnamed: IC1.2 (I), PAD3.1, R3.2
VCC: C11.2, C12.2, IC1.5 (VCC), IC2.5 (VCC), PAD5.1

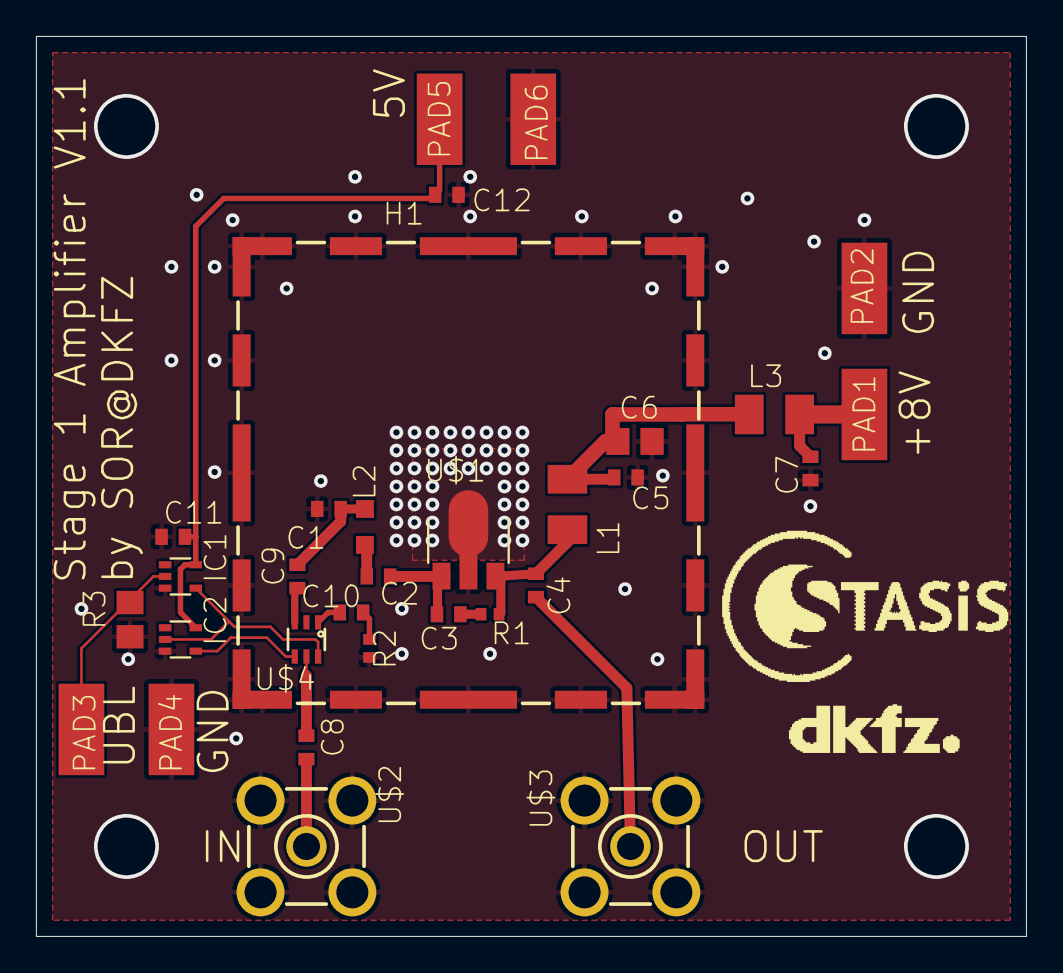
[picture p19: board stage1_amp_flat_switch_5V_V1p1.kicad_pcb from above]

Board: 2 copper layers, 55.0 x 50.0 mm, 33 parts (0 on the bottom side), 18 nets.

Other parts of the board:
U$5: LOGO_DKFZ
U$6: LOGO_STASIS

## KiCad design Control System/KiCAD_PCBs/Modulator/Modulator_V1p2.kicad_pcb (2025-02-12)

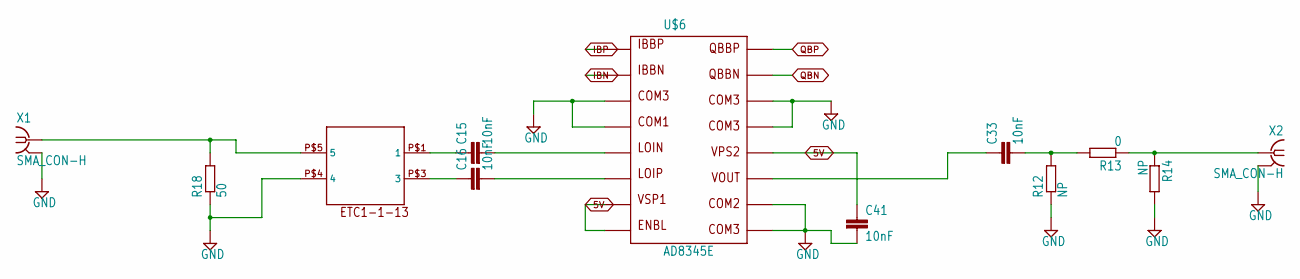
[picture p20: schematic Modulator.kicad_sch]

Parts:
C15, C16, C33: 10nF; C0402
C41: 10nF; C0603
R12, R14: NP; R0805
R13: 0; R0805
R18: 50; R0603
U$6: AD8345E; TSSOP16EXP
U$12: ETC1-1-13
X1, X2: SMA_CON-H; BU-SMA-H

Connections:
5V: C41.1, U$6.7, U$6.8, U$6.12; also elsewhere on the board
GND: C41.2, R12.1, R14.2, R18.1, U$6.3, U$6.4, U$6.9, U$6.10, U$6.13, U$6.14, U$6.EXP, U$12.P$4 (4), X1.2 (GND@1), X1.3 (GND@1), X1.4 (GND@1), X1.5 (GND@1), X2.2 (GND@1), X2.3 (GND@1), X2.4 (GND@1), X2.5 (GND@1); also elsewhere on the board
IBN: U$6.2; also elsewhere on the board
IBP: U$6.1; also elsewhere on the board
unnamed: C33.1, U$6.11
unnamed: C15.1, U$12.P$1 (1)
unnamed: C16.1, U$12.P$3 (3)
unnamed: R18.2, U$12.P$5 (5), X1.1
unnamed: C15.2, U$6.5
unnamed: C16.2, U$6.6
unnamed: R13.1, R14.1, X2.1
unnamed: C33.2, R12.2, R13.2
QBN: U$6.15; also elsewhere on the board
QBP: U$6.16; also elsewhere on the board

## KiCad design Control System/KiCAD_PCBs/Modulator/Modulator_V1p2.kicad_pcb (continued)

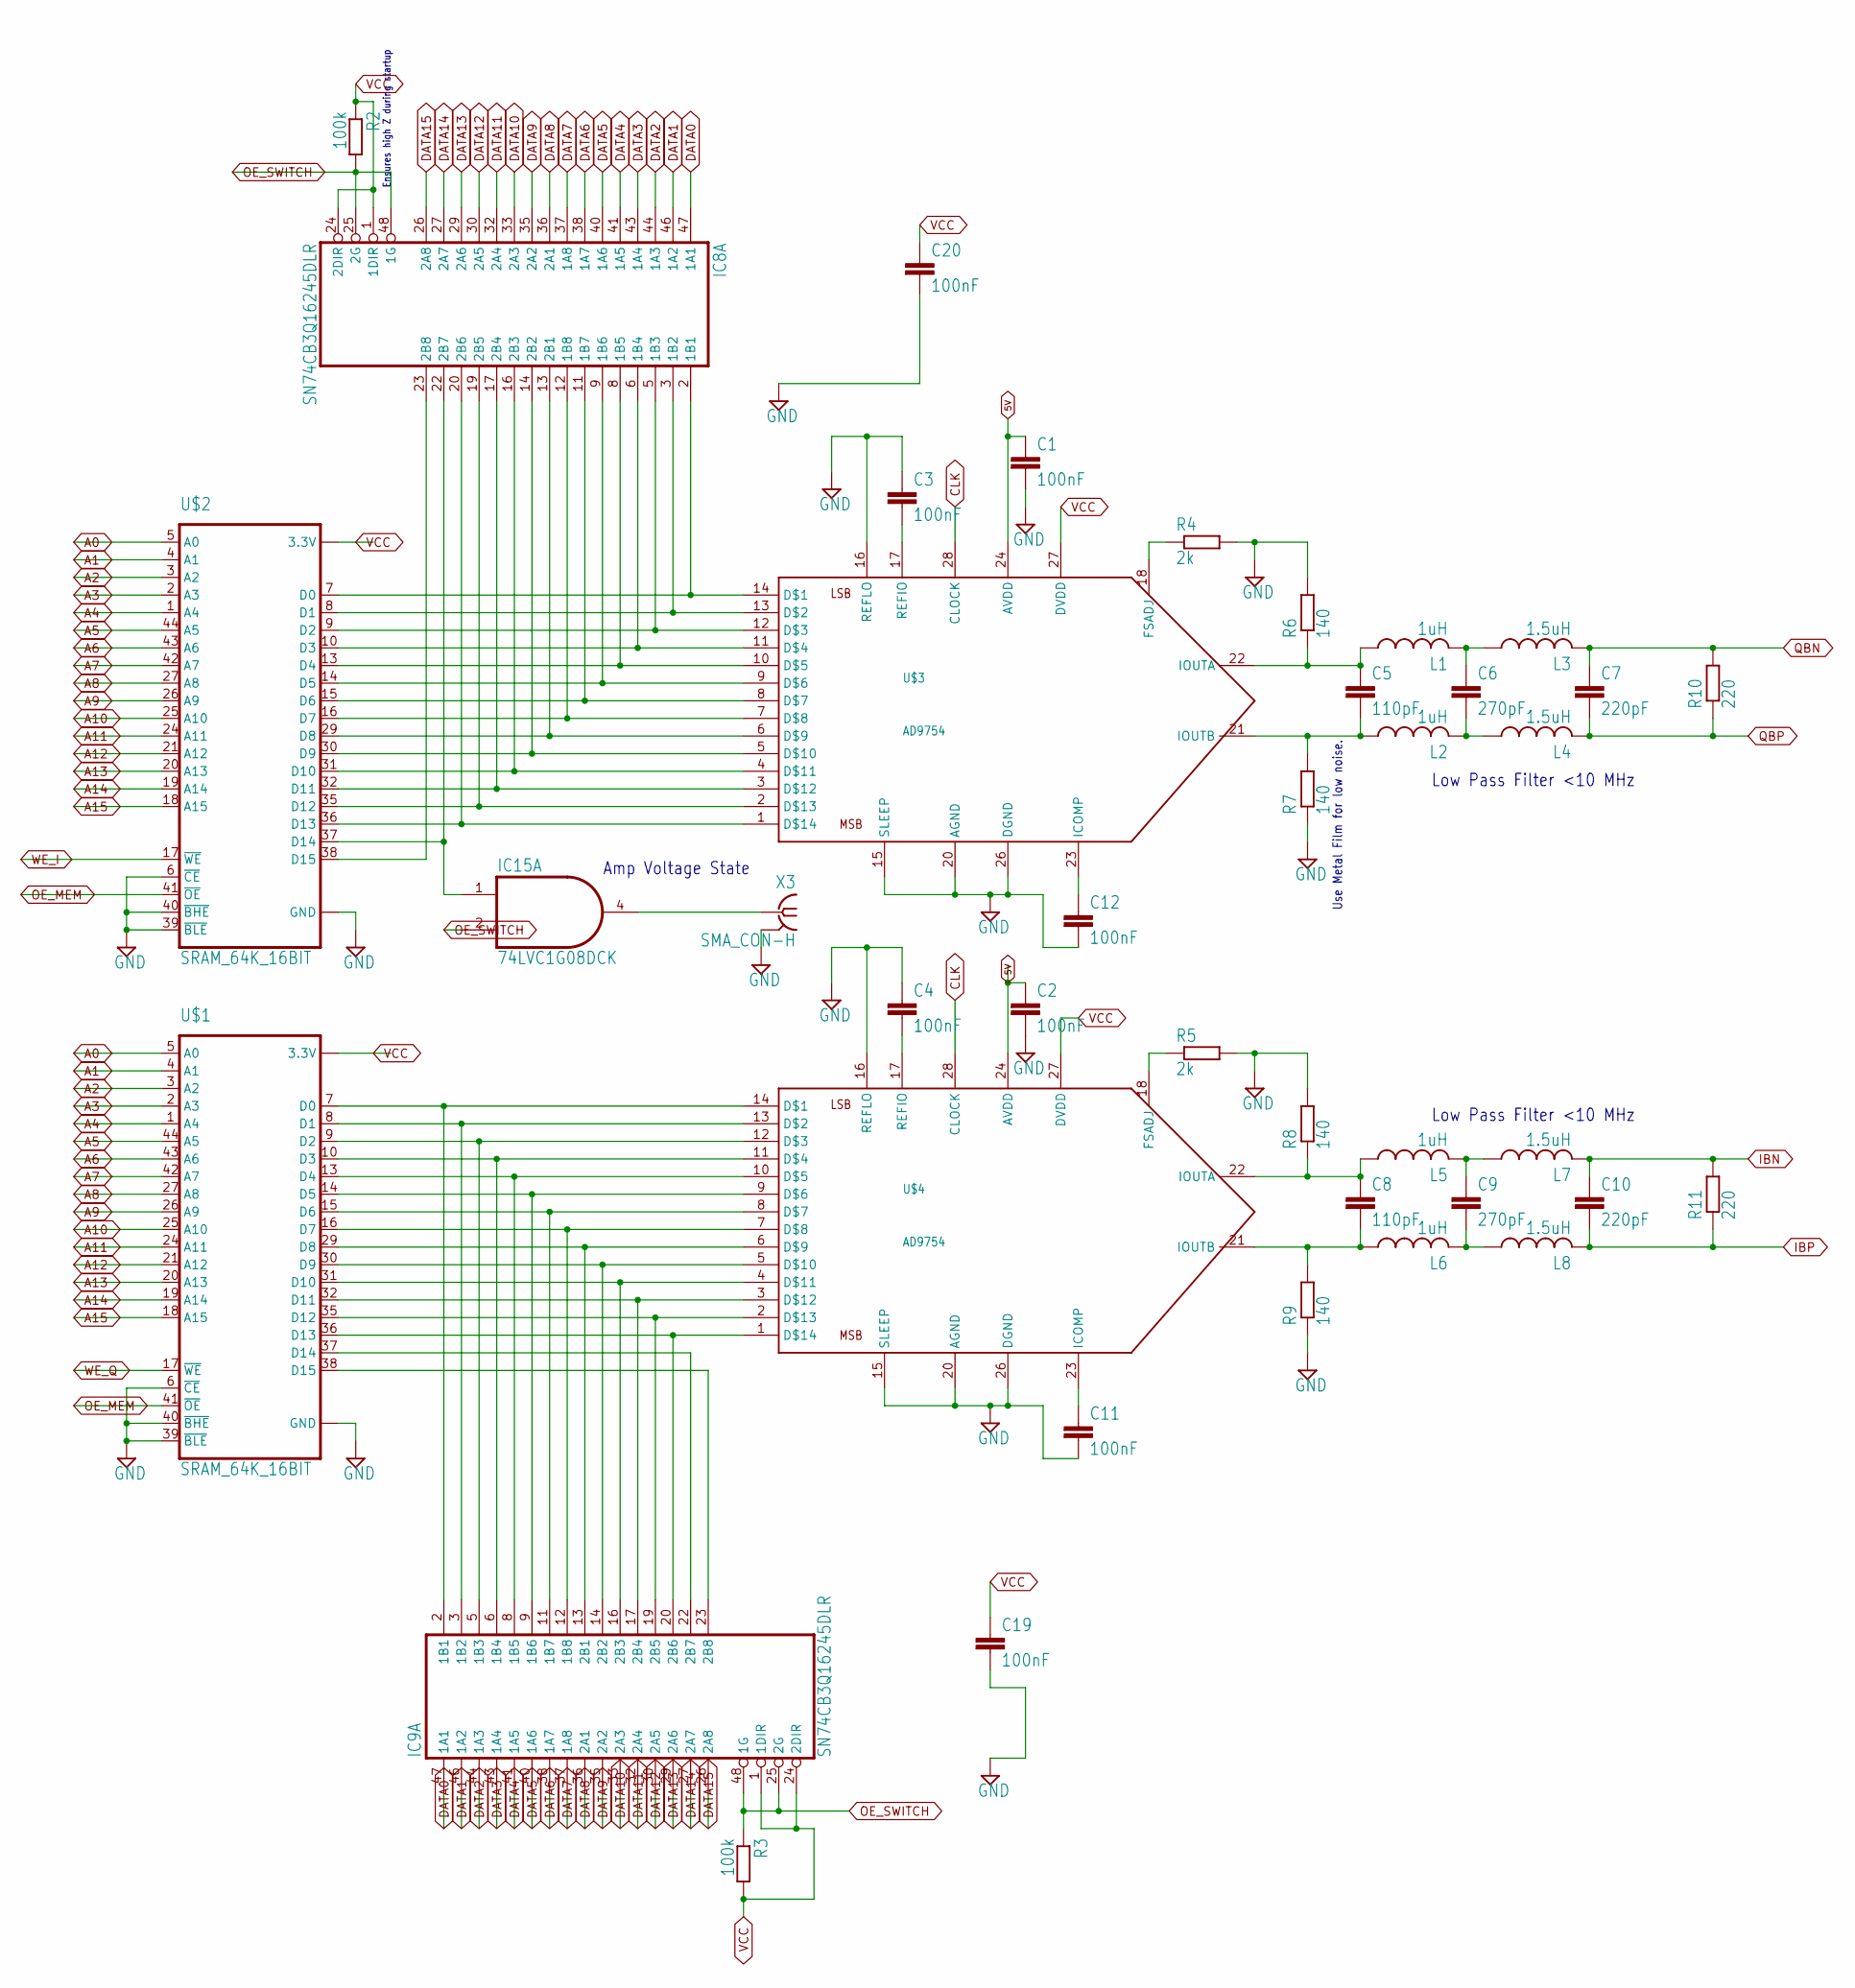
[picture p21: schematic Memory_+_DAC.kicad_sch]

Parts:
C1, C2, C3, C4, C11, C12, C19, C20: 100nF; C0603
C5, C8: 110pF; C0603
C6, C9: 270pF; C0603
C7, C10: 220pF; C0603
IC8, IC9: SN74CB3Q16245DLR; SSOP48DL
IC15: 74LVC1G08DCK; SC70-5
L1, L2, L5, L6: 1uH; L2012C
L3, L4, L7, L8: 1.5uH; L2012C
R2, R3: 100k; R0603
R4, R5: 2k; R0603
R6, R7, R8, R9: 140; R0603
R10, R11: 220; R0603
U$1, U$2: SRAM_64K_16BIT; TSOPII-Z44
U$3, U$4: AD9754; TSSOP28
X3: SMA_CON-H; BU-SMA-H

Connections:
5V: C1.1, C2.1, U$3.24 (AVDD), U$4.24 (AVDD); also elsewhere on the board
A0: U$1.5 (A0), U$2.5 (A0); also elsewhere on the board
A1: U$1.4 (A1), U$2.4 (A1); also elsewhere on the board
A2: U$1.3 (A2), U$2.3 (A2); also elsewhere on the board
A3: U$1.2 (A3), U$2.2 (A3); also elsewhere on the board
A4: U$1.1 (A4), U$2.1 (A4); also elsewhere on the board
A5: U$1.44 (A5), U$2.44 (A5); also elsewhere on the board
A6: U$1.43 (A6), U$2.43 (A6); also elsewhere on the board
A7: U$1.42 (A7), U$2.42 (A7); also elsewhere on the board
A8: U$1.27 (A8), U$2.27 (A8); also elsewhere on the board
A9: U$1.26 (A9), U$2.26 (A9); also elsewhere on the board
A10: U$1.25 (A10), U$2.25 (A10); also elsewhere on the board
A11: U$1.24 (A11), U$2.24 (A11); also elsewhere on the board
A12: U$1.21 (A12), U$2.21 (A12); also elsewhere on the board
A13: U$1.20 (A13), U$2.20 (A13); also elsewhere on the board
A14: U$1.19 (A14), U$2.19 (A14); also elsewhere on the board
A15: U$1.18 (A15), U$2.18 (A15); also elsewhere on the board
CLK: U$3.28 (CLOCK), U$4.28 (CLOCK); also elsewhere on the board
DATA0: IC8.47 (1A1), IC9.47 (1A1); also elsewhere on the board
DATA1: IC8.46 (1A2), IC9.46 (1A2); also elsewhere on the board
DATA2: IC8.44 (1A3), IC9.44 (1A3); also elsewhere on the board
DATA3: IC8.43 (1A4), IC9.43 (1A4); also elsewhere on the board
DATA4: IC8.41 (1A5), IC9.41 (1A5); also elsewhere on the board
DATA5: IC8.40 (1A6), IC9.40 (1A6); also elsewhere on the board
DATA6: IC8.38 (1A7), IC9.38 (1A7); also elsewhere on the board
DATA7: IC8.37 (1A8), IC9.37 (1A8); also elsewhere on the board
DATA8: IC8.36 (2A1), IC9.36 (2A1); also elsewhere on the board
DATA9: IC8.35 (2A2), IC9.35 (2A2); also elsewhere on the board
DATA10: IC8.33 (2A3), IC9.33 (2A3); also elsewhere on the board
DATA11: IC8.32 (2A4), IC9.32 (2A4); also elsewhere on the board
DATA12: IC8.30 (2A5), IC9.30 (2A5); also elsewhere on the board
DATA13: IC8.29 (2A6), IC9.29 (2A6); also elsewhere on the board
DATA14: IC8.27 (2A7), IC9.27 (2A7); also elsewhere on the board
DATA15: IC8.26 (2A8), IC9.26 (2A8); also elsewhere on the board
DI0: IC8.2 (1B1), U$2.7 (D0), U$3.14
DI1: IC8.3 (1B2), U$2.8 (D1), U$3.13
DI2: IC8.5 (1B3), U$2.9 (D2), U$3.12
DI3: IC8.6 (1B4), U$2.10 (D3), U$3.11
DI4: IC8.8 (1B5), U$2.13 (D4), U$3.10
DI5: IC8.9 (1B6), U$2.14 (D5), U$3.9
DI6: IC8.11 (1B7), U$2.15 (D6), U$3.8
DI7: IC8.12 (1B8), U$2.16 (D7), U$3.7
DI8: IC8.13 (2B1), U$2.29 (D8), U$3.6
DI9: IC8.14 (2B2), U$2.30 (D9), U$3.5
DI10: IC8.16 (2B3), U$2.31 (D10), U$3.4
DI11: IC8.17 (2B4), U$2.32 (D11), U$3.3
DI12: IC8.19 (2B5), U$2.35 (D12), U$3.2
DI13: IC8.20 (2B6), U$2.36 (D13), U$3.1
DQ0: IC9.2 (1B1), U$1.7 (D0), U$4.14
DQ1: IC9.3 (1B2), U$1.8 (D1), U$4.13
DQ2: IC9.5 (1B3), U$1.9 (D2), U$4.12
DQ3: IC9.6 (1B4), U$1.10 (D3), U$4.11
DQ4: IC9.8 (1B5), U$1.13 (D4), U$4.10
DQ5: IC9.9 (1B6), U$1.14 (D5), U$4.9
DQ6: IC9.11 (1B7), U$1.15 (D6), U$4.8
DQ7: IC9.12 (1B8), U$1.16 (D7), U$4.7
DQ8: IC9.13 (2B1), U$1.29 (D8), U$4.6
DQ9: IC9.14 (2B2), U$1.30 (D9), U$4.5
DQ10: IC9.16 (2B3), U$1.31 (D10), U$4.4
DQ11: IC9.17 (2B4), U$1.32 (D11), U$4.3
DQ12: IC9.19 (2B5), U$1.35 (D12), U$4.2
DQ13: IC9.20 (2B6), U$1.36 (D13), U$4.1
GND: C1.2, C2.2, C3.1, C4.1, C11.2, C12.2, C19.2, C20.2, IC8.4 (GND@1), IC8.10 (GND@2), IC8.15 (GND@3), IC8.21 (GND@4), IC8.28 (GND@5), IC8.34 (GND@6), IC8.39 (GND@7), IC8.45 (GND@8), IC9.4 (GND@1), IC9.10 (GND@2), IC9.15 (GND@3), IC9.21 (GND@4), IC9.28 (GND@5), IC9.34 (GND@6), IC9.39 (GND@7), IC9.45 (GND@8), IC15.3 (GND), R4.2, R5.2, R6.2, R7.1, R8.2, R9.1, U$1.6 (~CE), U$1.12 (GND), U$1.34 (GND), U$1.39 (~BLE), U$1.40 (~BHE), U$2.6 (~CE), U$2.12 (GND), U$2.34 (GND), U$2.39 (~BLE), U$2.40 (~BHE), U$3.15 (SLEEP), U$3.16 (REFLO), U$3.20 (AGND), U$3.26 (DGND), U$4.15 (SLEEP), U$4.16 (REFLO), U$4.20 (AGND), U$4.26 (DGND), X3.2 (GND@1), X3.3 (GND@1), X3.4 (GND@1), X3.5 (GND@1); also elsewhere on the board
IBN: C10.1, L7.2, R11.2; also elsewhere on the board
IBP: C10.2, L8.2, R11.1; also elsewhere on the board
unnamed: IC8.22 (2B7), IC15.1 (I0), U$2.37 (D14)
unnamed: IC8.23 (2B8), U$2.38 (D15)
unnamed: IC9.22 (2B7), U$1.37 (D14)
unnamed: IC9.23 (2B8), U$1.38 (D15)
unnamed: R5.1, U$4.18 (FSADJ)
unnamed: IC15.4 (O), X3.1
unnamed: C6.1, L1.2, L3.1
unnamed: R4.1, U$3.18 (FSADJ)
unnamed: C6.2, L2.2, L4.1
unnamed: C3.2, U$3.17 (REFIO)
unnamed: C4.2, U$4.17 (REFIO)
unnamed: C8.1, L5.1, R8.1, U$4.22 (IOUTA)
unnamed: C8.2, L6.1, R9.2, U$4.21 (IOUTB)
unnamed: C5.1, L1.1, R6.1, U$3.22 (IOUTA)
unnamed: C9.1, L5.2, L7.1
unnamed: C5.2, L2.1, R7.2, U$3.21 (IOUTB)
unnamed: C11.1, U$4.23 (ICOMP)
unnamed: C9.2, L6.2, L8.1
unnamed: C12.1, U$3.23 (ICOMP)
OE_MEM: U$1.41 (~OE), U$2.41 (~OE); also elsewhere on the board
OE_SWITCH: IC8.25 (2G), IC8.48 (1G), IC9.25 (2G), IC9.48 (1G), IC15.2 (I1), R2.2, R3.1; also elsewhere on the board
QBN: C7.1, L3.2, R10.2; also elsewhere on the board
QBP: C7.2, L4.2, R10.1; also elsewhere on the board
VCC: C19.1, C20.1, IC8.1 (1DIR), IC8.7 (VCC@1), IC8.18 (VCC@2), IC8.24 (2DIR), IC8.31 (VCC@3), IC8.42 (VCC@4), IC9.1 (1DIR), IC9.7 (VCC@1), IC9.18 (VCC@2), IC9.24 (2DIR), IC9.31 (VCC@3), IC9.42 (VCC@4), IC15.5 (VCC), R2.1, R3.2, U$1.11 (3.3V), U$1.33 (3.3V), U$2.11 (3.3V), U$2.33 (3.3V), U$3.27 (DVDD), U$4.27 (DVDD); also elsewhere on the board
WE_I: U$2.17 (~WE); also elsewhere on the board
WE_Q: U$1.17 (~WE); also elsewhere on the board

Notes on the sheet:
Low Pass Filter <10 MHz
Amp Voltage State
Ensures high Z during startup
Use Metal Film for low noise.

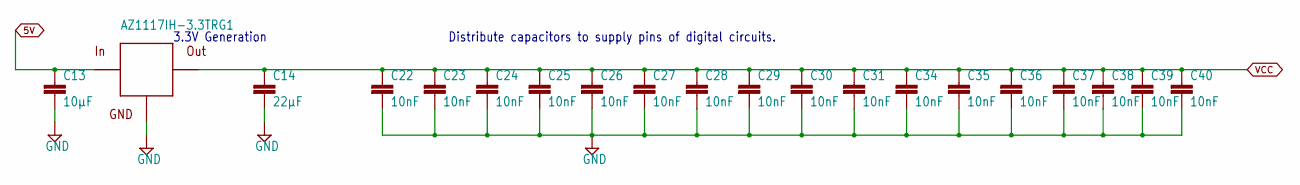
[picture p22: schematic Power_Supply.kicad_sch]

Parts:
C13: 10µF; C1206
C14: 22µF; C1206
C22, C23, C24, C25, C26, C27, C28, C29, C30, C31, C34, C35, C36, C37, C38, C39, C40: 10nF; C0603
U$9: AZ1117IH-3.3TRG1; SOT223

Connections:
5V: C13.1, U$9.3 (IN); also elsewhere on the board
GND: C13.2, C14.2, C22.2, C23.2, C24.2, C25.2, C26.2, C27.2, C28.2, C29.2, C30.2, C31.2, C34.2, C35.2, C36.2, C37.2, C38.2, C39.2, C40.2, U$9.1 (GND); also elsewhere on the board
VCC: C14.1, C22.1, C23.1, C24.1, C25.1, C26.1, C27.1, C28.1, C29.1, C30.1, C31.1, C34.1, C35.1, C36.1, C37.1, C38.1, C39.1, C40.1, U$9.2 (OUT), U$9.4 (OUT); also elsewhere on the board

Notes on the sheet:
Distribute capacitors to supply pins of digital circuits.
3.3V Generation

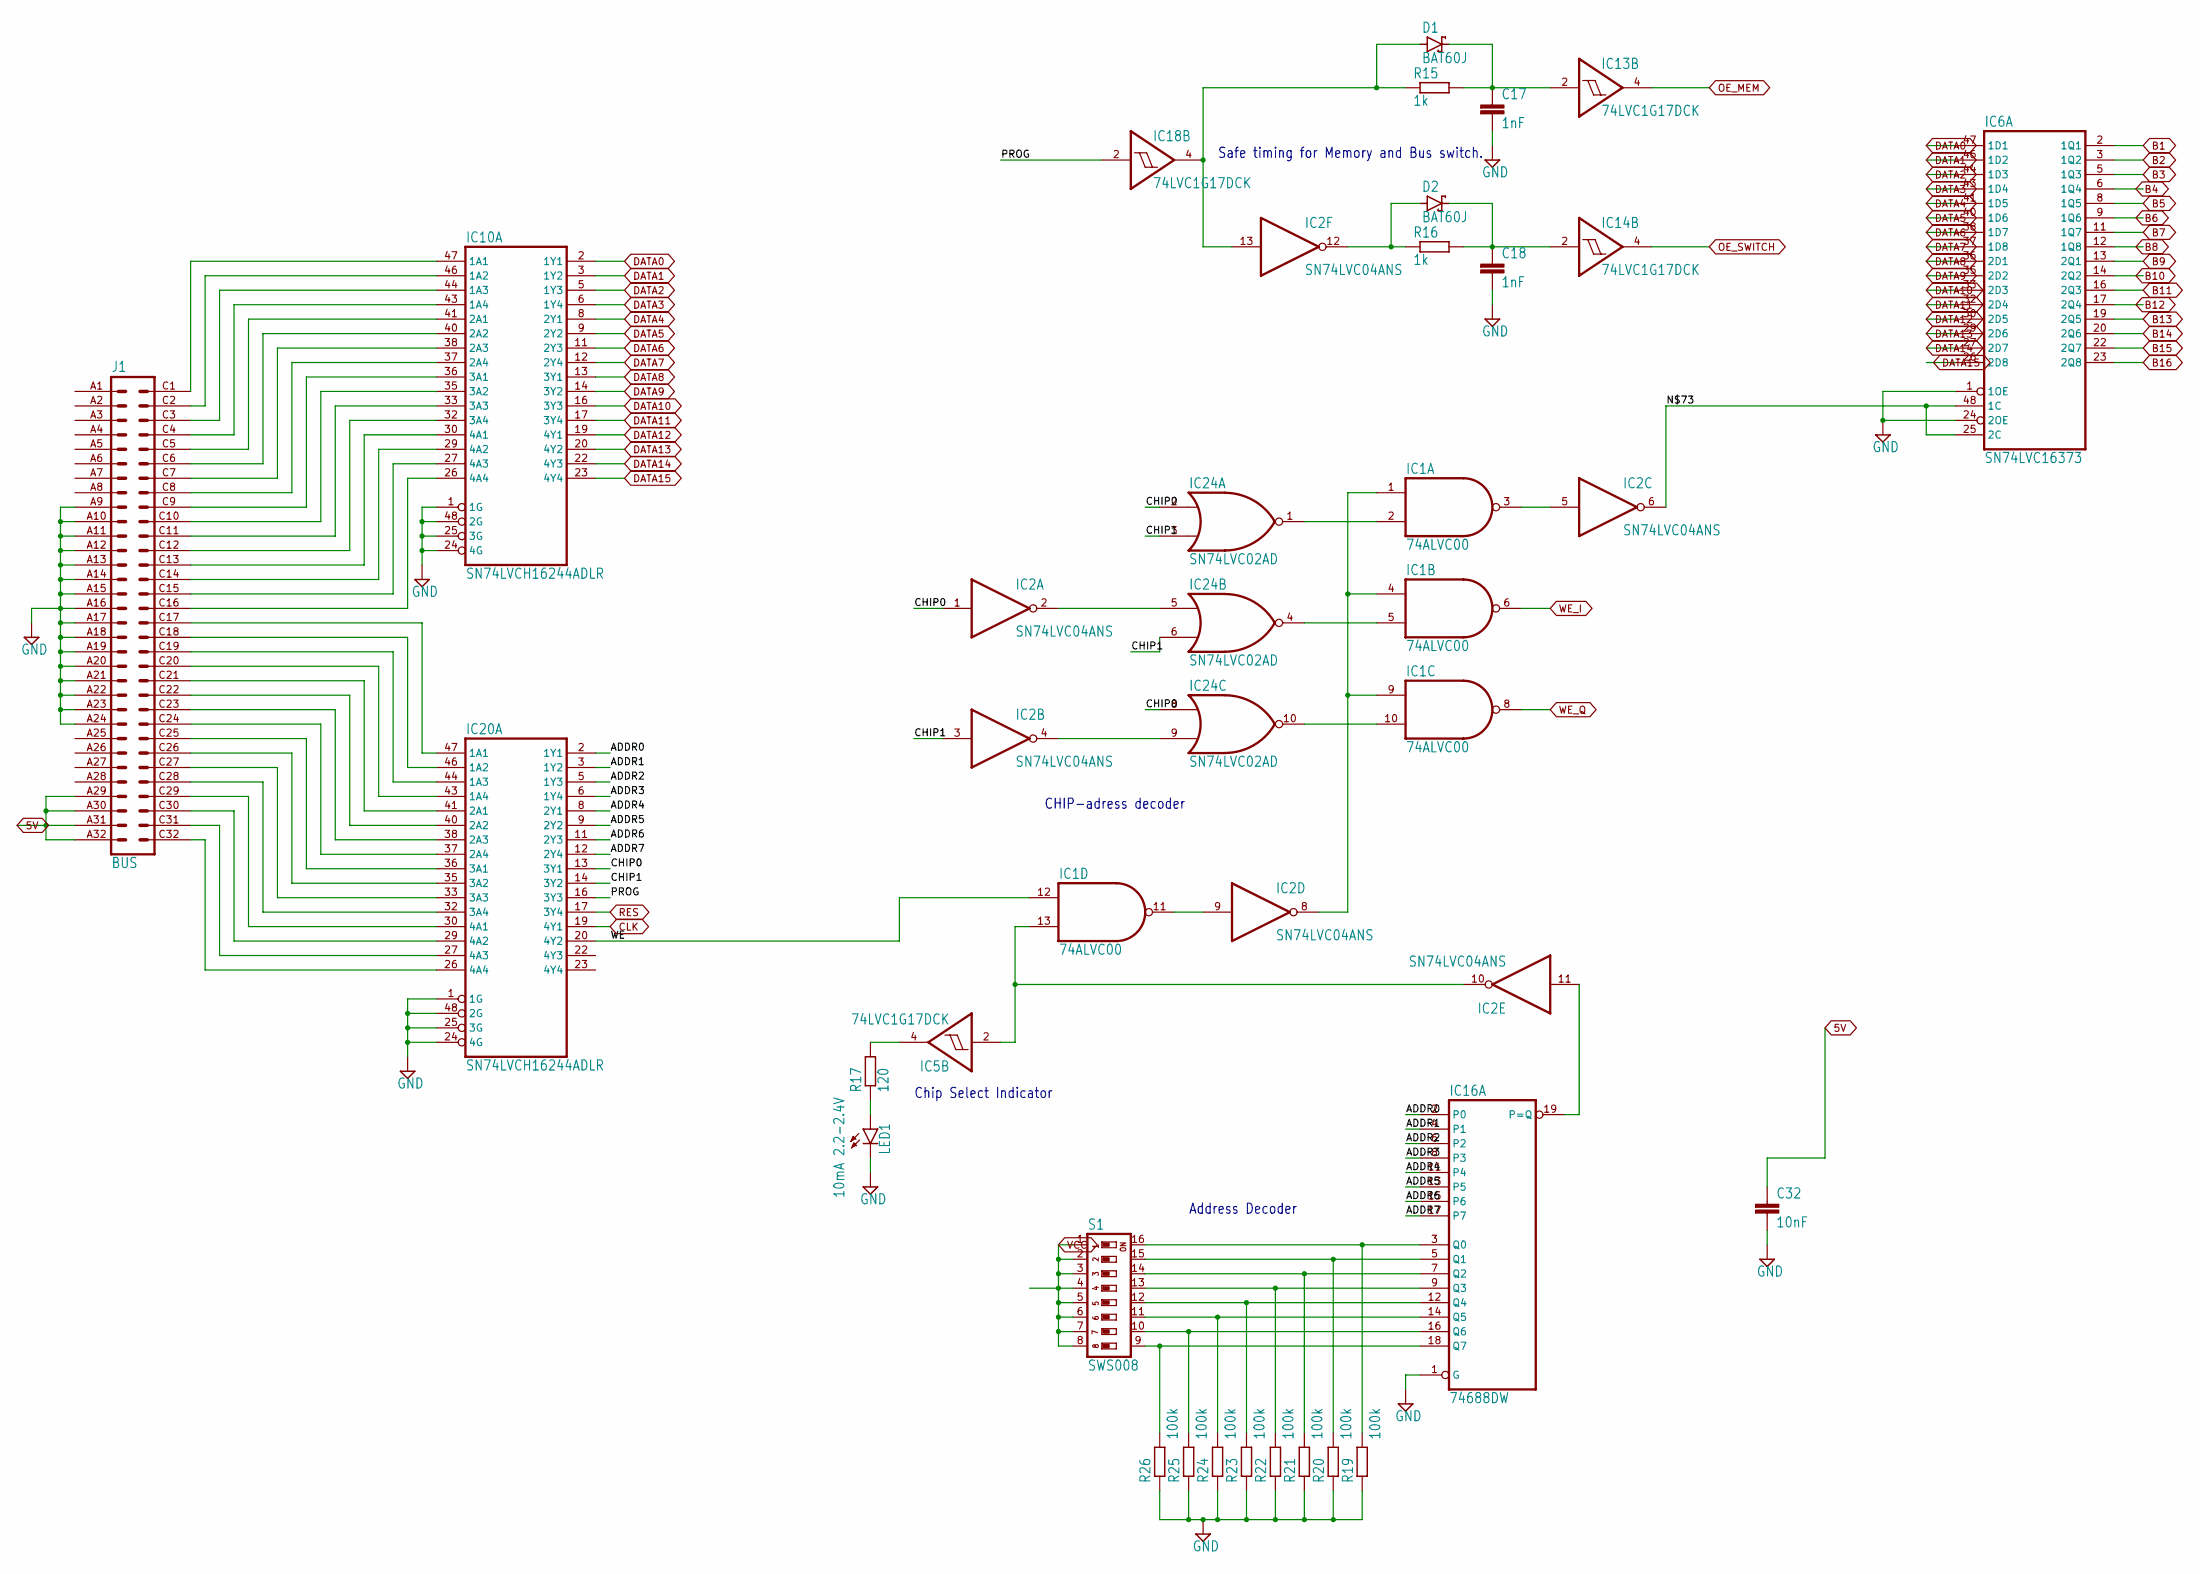
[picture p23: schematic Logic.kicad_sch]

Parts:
C17, C18: 1nF; C0805
C32: 10nF; C0603
D1, D2: BAT60J; SOD323_ST
IC1: 74ALVC00; SO14
IC2: SN74LVC04ANS; SO14
IC5, IC13, IC14, IC18: 74LVC1G17DCK; SC70-5
IC6: SN74LVC16373; SSOP48DL
IC10, IC20: SN74LVCH16244ADLR; SSOP48DL
IC16: 74688DW; SO20W
IC24: SN74LVC02AD; SO14
J1: BUS; VG64B
LED1: 10mA 2.2-2.4V; LED3MM
R15, R16: 1k; R0603
R17: 120; R0603
R19, R20, R21, R22, R23, R24, R25, R26: 100k; R0603
S1: SWS008; SMS-008

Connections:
5V: C32.1, J1.A29, J1.A30, J1.A31, J1.A32; also elsewhere on the board
ADDR0: IC16.2 (P0), IC20.2 (1Y1)
ADDR1: IC16.4 (P1), IC20.3 (1Y2)
ADDR2: IC16.6 (P2), IC20.5 (1Y3)
ADDR3: IC16.8 (P3), IC20.6 (1Y4)
ADDR4: IC16.11 (P4), IC20.8 (2Y1)
ADDR5: IC16.13 (P5), IC20.9 (2Y2)
ADDR6: IC16.15 (P6), IC20.11 (2Y3)
ADDR7: IC16.17 (P7), IC20.12 (2Y4)
B1: IC6.2 (1Q1); also elsewhere on the board
B2: IC6.3 (1Q2); also elsewhere on the board
B3: IC6.5 (1Q3); also elsewhere on the board
B4: IC6.6 (1Q4); also elsewhere on the board
B5: IC6.8 (1Q5); also elsewhere on the board
B6: IC6.9 (1Q6); also elsewhere on the board
B7: IC6.11 (1Q7); also elsewhere on the board
B8: IC6.12 (1Q8); also elsewhere on the board
B9: IC6.13 (2Q1); also elsewhere on the board
B10: IC6.14 (2Q2); also elsewhere on the board
B11: IC6.16 (2Q3); also elsewhere on the board
B12: IC6.17 (2Q4); also elsewhere on the board
B13: IC6.19 (2Q5); also elsewhere on the board
B14: IC6.20 (2Q6); also elsewhere on the board
B15: IC6.22 (2Q7); also elsewhere on the board
B16: IC6.23 (2Q8); also elsewhere on the board
CHIP0: IC2.1 (I), IC20.13 (3Y1), IC24.2 (I0), IC24.8 (I0)
CHIP1: IC2.3 (I), IC20.14 (3Y2), IC24.3 (I1), IC24.6 (I1)
CLK: IC20.19 (4Y1); also elsewhere on the board
DATA0: IC6.47 (1D1), IC10.2 (1Y1); also elsewhere on the board
DATA1: IC6.46 (1D2), IC10.3 (1Y2); also elsewhere on the board
DATA2: IC6.44 (1D3), IC10.5 (1Y3); also elsewhere on the board
DATA3: IC6.43 (1D4), IC10.6 (1Y4); also elsewhere on the board
DATA4: IC6.41 (1D5), IC10.8 (2Y1); also elsewhere on the board
DATA5: IC6.40 (1D6), IC10.9 (2Y2); also elsewhere on the board
DATA6: IC6.38 (1D7), IC10.11 (2Y3); also elsewhere on the board
DATA7: IC6.37 (1D8), IC10.12 (2Y4); also elsewhere on the board
DATA8: IC6.36 (2D1), IC10.13 (3Y1); also elsewhere on the board
DATA9: IC6.35 (2D2), IC10.14 (3Y2); also elsewhere on the board
DATA10: IC6.33 (2D3), IC10.16 (3Y3); also elsewhere on the board
DATA11: IC6.32 (2D4), IC10.17 (3Y4); also elsewhere on the board
DATA12: IC6.30 (2D5), IC10.19 (4Y1); also elsewhere on the board
DATA13: IC6.29 (2D6), IC10.20 (4Y2); also elsewhere on the board
DATA14: IC6.27 (2D7), IC10.22 (4Y3); also elsewhere on the board
DATA15: IC6.26 (2D8), IC10.23 (4Y4); also elsewhere on the board
GND: C17.2, C18.2, C32.2, IC1.7 (GND), IC2.7 (GND), IC5.3 (GND), IC6.1 (1OE), IC6.4 (GND@1), IC6.10 (GND@2), IC6.15 (GND@3), IC6.21 (GND@4), IC6.24 (2OE), IC6.28 (GND@5), IC6.34 (GND@6), IC6.39 (GND@7), IC6.45 (GND@8), IC10.1 (1G), IC10.4 (GND@1), IC10.10 (GND@2), IC10.15 (GND@3), IC10.21 (GND@4), IC10.24 (4G), IC10.25 (3G), IC10.28 (GND@5), IC10.34 (GND@6), IC10.39 (GND@7), IC10.45 (GND@8), IC10.48 (2G), IC13.3 (GND), IC14.3 (GND), IC16.1 (G), IC16.10 (GND), IC18.3 (GND), IC20.1 (1G), IC20.4 (GND@1), IC20.10 (GND@2), IC20.15 (GND@3), IC20.21 (GND@4), IC20.24 (4G), IC20.25 (3G), IC20.28 (GND@5), IC20.34 (GND@6), IC20.39 (GND@7), IC20.45 (GND@8), IC20.48 (2G), IC24.7 (GND), J1.A9, J1.A10, J1.A11, J1.A12, J1.A13, J1.A14, J1.A15, J1.A16, J1.A17, J1.A18, J1.A19, J1.A20, J1.A21, J1.A22, J1.A23, J1.A24, LED1.K (C), R19.1, R20.1, R21.1, R22.1, R23.1, R24.1, R25.1, R26.1; also elsewhere on the board
unnamed: IC10.47 (1A1), J1.C1
unnamed: IC10.46 (1A2), J1.C2
unnamed: C17.1, D1.C, IC13.2 (I), R15.2
unnamed: IC10.44 (1A3), J1.C3
unnamed: IC10.43 (1A4), J1.C4
unnamed: IC10.41 (2A1), J1.C5
unnamed: IC10.40 (2A2), J1.C6
unnamed: IC10.38 (2A3), J1.C7
unnamed: IC10.37 (2A4), J1.C8
unnamed: IC10.36 (3A1), J1.C9
unnamed: IC10.35 (3A2), J1.C10
unnamed: IC10.33 (3A3), J1.C11
unnamed: IC10.32 (3A4), J1.C12
unnamed: IC10.30 (4A1), J1.C13
unnamed: IC10.29 (4A2), J1.C14
unnamed: IC10.27 (4A3), J1.C15
unnamed: IC10.26 (4A4), J1.C16
unnamed: IC20.47 (1A1), J1.C17
unnamed: IC20.46 (1A2), J1.C18
unnamed: IC20.44 (1A3), J1.C19
unnamed: IC20.43 (1A4), J1.C20
unnamed: IC20.41 (2A1), J1.C21
unnamed: IC20.40 (2A2), J1.C22
unnamed: IC20.38 (2A3), J1.C23
unnamed: IC20.37 (2A4), J1.C24
unnamed: IC20.36 (3A1), J1.C25
unnamed: IC20.35 (3A2), J1.C26
unnamed: IC20.33 (3A3), J1.C27
unnamed: IC16.3 (Q0), R19.2, S1.16
unnamed: C18.1, D2.C, IC14.2 (I), R16.2
unnamed: D2.A, IC2.12 (O), R16.1
unnamed: IC16.5 (Q1), R20.2, S1.15
unnamed: IC16.7 (Q2), R21.2, S1.14
unnamed: IC16.9 (Q3), R22.2, S1.13
unnamed: IC16.12 (Q4), R23.2, S1.12
unnamed: IC16.14 (Q5), R24.2, S1.11
unnamed: IC16.16 (Q6), R25.2, S1.10
unnamed: IC16.18 (Q7), R26.2, S1.9
unnamed: IC1.2 (I1), IC24.1 (O)
unnamed: IC1.5 (I1), IC24.4 (O)
unnamed: IC2.6 (O), IC6.25 (2C), IC6.48 (1C)
unnamed: D1.A, IC2.13 (I), IC18.4 (O), R15.1
unnamed: IC2.2 (O), IC24.5 (I0)
unnamed: IC2.4 (O), IC24.9 (I1)
unnamed: IC20.32 (3A4), J1.C28
unnamed: IC1.10 (I1), IC24.10 (O)
unnamed: IC1.3 (O), IC2.5 (I)
unnamed: IC2.11 (I), IC16.19 (P=Q)
unnamed: IC1.13 (I1), IC2.10 (O), IC5.2 (I)
unnamed: IC1.1 (I0), IC1.4 (I0), IC1.9 (I0), IC2.8 (O)
unnamed: IC1.11 (O), IC2.9 (I)
unnamed: IC20.30 (4A1), J1.C29
unnamed: IC20.29 (4A2), J1.C30
unnamed: IC20.27 (4A3), J1.C31
unnamed: IC20.26 (4A4), J1.C32
unnamed: LED1.A, R17.1
unnamed: IC5.4 (O), R17.2
OE_MEM: IC13.4 (O); also elsewhere on the board
OE_SWITCH: IC14.4 (O); also elsewhere on the board
PROG: IC18.2 (I), IC20.16 (3Y3)
RES: IC20.17 (3Y4); also elsewhere on the board
VCC: IC1.14 (VCC), IC2.14 (VCC), IC5.5 (VCC), IC6.7 (VCC@1), IC6.18 (VCC@2), IC6.31 (VCC@3), IC6.42 (VCC@4), IC10.7 (VCC@1), IC10.18 (VCC@2), IC10.31 (VCC@3), IC10.42 (VCC@4), IC13.5 (VCC), IC14.5 (VCC), IC16.20 (VCC), IC18.5 (VCC), IC20.7 (VCC@1), IC20.18 (VCC@2), IC20.31 (VCC@3), IC20.42 (VCC@4), IC24.14 (VCC), S1.1, S1.2, S1.3, S1.4, S1.5, S1.6, S1.7, S1.8; also elsewhere on the board
WE: IC1.12 (I0), IC20.20 (4Y2)
WE_I: IC1.6 (O); also elsewhere on the board
WE_Q: IC1.8 (O); also elsewhere on the board

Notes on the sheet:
Address Decoder
Chip Select Indicator
Safe timing for Memory and Bus switch.
CHIP-adress decoder


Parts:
C21: 10nF; C0603
IC3, IC4: 74688DW; SO20W
IC7: SN74LVC1G32IDCKREP; SC70-5
IC11: 741G04DCK; SC70-5
IC24: SN74LVC02AD; SO14
JP1: PINHD-2X4; 2X04
R1: 100k; R0603
U$5: DS1100LZ-20LZ; SO-08
U$7, U$8: 74LV393PW; TSSOP14

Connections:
A0: IC3.2 (P0), U$7.3 (QA); also elsewhere on the board
A1: IC3.4 (P1), U$7.4 (QB); also elsewhere on the board
A2: IC3.6 (P2), U$7.5 (QC); also elsewhere on the board
A3: IC3.8 (P3), U$7.6 (QD), U$7.13 (A); also elsewhere on the board
A4: IC3.11 (P4), U$7.11 (QA); also elsewhere on the board
A5: IC3.13 (P5), U$7.10 (QB); also elsewhere on the board
A6: IC3.15 (P6), U$7.9 (QC); also elsewhere on the board
A7: IC3.17 (P7), U$7.8 (QD), U$8.1 (A); also elsewhere on the board
A8: IC4.2 (P0), U$8.3 (QA); also elsewhere on the board
A9: IC4.4 (P1), U$8.4 (QB); also elsewhere on the board
A10: IC4.6 (P2), U$8.5 (QC); also elsewhere on the board
A11: IC4.8 (P3), U$8.6 (QD), U$8.13 (A); also elsewhere on the board
A12: IC4.11 (P4), U$8.11 (QA); also elsewhere on the board
A13: IC4.13 (P5), U$8.10 (QB); also elsewhere on the board
A14: IC4.15 (P6), U$8.9 (QC); also elsewhere on the board
A15: IC4.17 (P7), U$8.8 (QD); also elsewhere on the board
B1: IC3.3 (Q0); also elsewhere on the board
B2: IC3.5 (Q1); also elsewhere on the board
B3: IC3.7 (Q2); also elsewhere on the board
B4: IC3.9 (Q3); also elsewhere on the board
B5: IC3.12 (Q4); also elsewhere on the board
B6: IC3.14 (Q5); also elsewhere on the board
B7: IC3.16 (Q6); also elsewhere on the board
B8: IC3.18 (Q7); also elsewhere on the board
B9: IC4.3 (Q0); also elsewhere on the board
B10: IC4.5 (Q1); also elsewhere on the board
B11: IC4.7 (Q2); also elsewhere on the board
B12: IC4.9 (Q3); also elsewhere on the board
B13: IC4.12 (Q4); also elsewhere on the board
B14: IC4.14 (Q5); also elsewhere on the board
B15: IC4.16 (Q6); also elsewhere on the board
B16: IC4.18 (Q7); also elsewhere on the board
CLK: IC11.2 (I); also elsewhere on the board
CLR: IC7.4 (O), U$7.2 (CLR), U$7.12 (CLR), U$8.2 (CLR), U$8.12 (CLR)
GND: C21.2, IC3.1 (G), IC3.10 (GND), IC4.1 (G), IC4.10 (GND), IC7.3 (GND), IC11.3 (GND), IC24.7 (GND), R1.2, U$5.4 (GND), U$7.7 (GND), U$8.7 (GND); also elsewhere on the board
IS_EQUAL: IC7.2 (I1), IC24.13 (O)
unnamed: IC3.19 (P=Q), IC24.11 (I0)
unnamed: IC4.19 (P=Q), IC24.12 (I1)
unnamed: JP1.2, JP1.4, JP1.6, JP1.8, U$7.1 (A)
unnamed: IC11.4 (O), U$5.1 (CLK_IN)
unnamed: JP1.1, U$5.7 (4NS)
unnamed: JP1.3, U$5.2 (8NS)
unnamed: JP1.5, U$5.6 (12NS)
unnamed: JP1.7, U$5.3 (16NS)
RES: IC7.1 (I0), R1.1; also elsewhere on the board
VCC: C21.1, IC3.20 (VCC), IC4.20 (VCC), IC7.5 (VCC), IC11.5 (VCC), IC24.14 (VCC), U$5.8 (3.3V), U$7.14 (VCC), U$8.14 (VCC); also elsewhere on the board

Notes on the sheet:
DAC reacts on rising, Counter on falling flank
Delay Clock, so that data is read from memory to DAC before counter switches to new address


Board: 6 copper layers, 160.0 x 100.0 mm, 114 parts (0 on the bottom side), 195 nets.

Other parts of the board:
U$10: LOGO_DKFZ
U$11: LOGO_STASIS

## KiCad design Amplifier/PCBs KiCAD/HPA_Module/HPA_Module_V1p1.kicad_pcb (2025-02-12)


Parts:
C1, C16: 56pF; C1210
C2, C3: 560pF; C1210
C4, C17: JZ100; CTRIM3018_12
C5: 7pF; C1210K
C6: 180pF; C0805
C7: 1.8nF (S_res=128Mhz); C1210
C8: 120pF; C1210
C9: 33pF; C2220K
C10: 90pF; C2220K
C11, C12: 470pF; C1210
C13: 1.8nF; C1210
C14: 47pF; C1210
C15, C19: 10nF; C0805
C18: 1nF; C0805
C20: 8 Windings 4mm wire; C1210K
IC1: 741G14DBV; SOT23-5
L1, L2: LQW2UASR33G00L; L2825P
L3, L6: 1111SQ-27NGEC; L2825P
L4, L5: GA3093-ALC; L4532P
L7: GA3094-ALC; L4532P
PAD1, PAD2, PAD3, PAD4, PAD5, PAD6, PAD7, PAD8, PAD9, PAD10, PAD11, PAD12, PAD13, PAD18, PAD19: SMD5; SMD2,54-5,08
Q1: 310mA/60V/1.6Ω; SOT323
R1: 3224W-1-501E; RTRIM3224W
R2: 180; R0805
R3: 220; R0805
R4, R5: 0; R1206
U$1: MRFX1K80; NI-1230H-4S
U$2, U$3: COAX_CON_DIRECT; COAX.141

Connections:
GND: C1.2, C6.2, C7.2, C8.2, C13.2, C15.2, C17.- (A), C18.1, C19.1, C20.1, IC1.3 (GND), L6.1, PAD1.1, PAD3.1, PAD4.1, PAD8.1, PAD19.1, Q1.2 (S), R1.1 (A), U$2.P$2 (GND@1), U$3.P$2 (GND@1)
unnamed: L1.2, L7.2, R5.2, U$1.P$4 (GB)
unnamed: L2.1, L7.1, R4.2, U$1.P$3 (GA)
unnamed: C18.2, C19.2, L1.1, L2.2, PAD13.1
unnamed: C9.1, C10.1, C11.1, L4.1, U$1.P$1 (DA)
unnamed: C1.1, C2.1, L3.2
unnamed: C3.1, C16.1, L6.2
unnamed: C4.- (A), C5.2, C16.2, C17.+ (E), C20.2, L3.1
unnamed: C9.2, C10.2, C12.1, L5.2, U$1.P$2 (DB)
unnamed: C4.+ (E), C5.1, U$2.P$1 (1)
unnamed: C7.1, C8.1, L4.2, L5.1, PAD9.1
unnamed: C6.1, Q1.3 (D), R2.1, R3.1
unnamed: C11.2, PAD5.1
unnamed: C12.2, PAD6.1
unnamed: C13.1, PAD10.1, PAD18.1
unnamed: R1.2 (S), R3.2
unnamed: C14.1, PAD7.1
unnamed: C14.2, U$3.P$1 (1)
unnamed: IC1.4 (O), Q1.1 (G)
unnamed: PAD12.1, R2.2
unnamed: IC1.2 (I), PAD11.1
unnamed: C2.2, R4.1
unnamed: C3.2, R5.1
VCC: C15.1, IC1.5 (VCC), PAD2.1, R1.3 (E)

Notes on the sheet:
Wirebridge 0.5x10 mm
10mm
6.6nH
7mm wide, 60mm long
5mm
3mm
wire, diam. 1.9mm, with Ferrite
Balun, 50 Ohm SR .141
|Z| = 200 Ohm
12nH


Board: 2 copper layers, 160.0 x 100.0 mm, 54 parts (0 on the bottom side), 24 nets.

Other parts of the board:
U$4: LOGO_DKFZ
U$5: LOGO_STASIS

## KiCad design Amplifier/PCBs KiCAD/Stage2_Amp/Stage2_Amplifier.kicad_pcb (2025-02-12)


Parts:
C1, C7: 1-10pF; CTRIMTZBX4
C2: 15pF; C1210
C3: 5pF; C1210
C4: 10nF; C1206
C5: 1nF; C1206
C6: 1nF; C0805
C15: 10nF; C0805
IC1: 74LVC1G14DBV; SOT23-5
L1: 39nH (1111SQ-39NGEC); L3225P
L2: L-USL3225P; L3225P
PAD1, PAD2, PAD3, PAD4, PAD5, PAD11: SMD5; SMD2,54-5,08
Q1: 2N7002PW; SOT323
R1: 1; R1206
R2: 2; R1206
R3: 3224W-1-501E; RTRIM3224W
R4: 47k; R0805
R5: 220; R0805
U$1: MRFE6VS25NR1; TO-270_ONBOARD
U$2, U$3: COAX_CON_DIRECT; COAX.141

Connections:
GND: C4.2, C5.2, C6.2, C15.2, IC1.3 (GND), PAD3.1, PAD4.1, PAD5.1, Q1.2 (S), R3.1 (A), R4.2, U$1.P$3 (GND), U$2.P$2 (GND@1), U$3.P$2 (GND@1)
unnamed: R2.1, U$1.P$2 (IN)
unnamed: C1.2 (A), C3.2, L1.2, R2.2
unnamed: L1.1, R1.1
unnamed: C2.1, C7.1 (E), L2.2, U$1.P$1 (OUT)
unnamed: C1.1 (E), C3.1, U$2.P$1 (1)
unnamed: C2.2, C7.2 (A), U$3.P$1 (1)
unnamed: C4.1, C5.1, L2.1, PAD1.1
unnamed: C6.1, Q1.3 (D), R1.2, R5.1
unnamed: R3.2 (S), R5.2
unnamed: IC1.4 (O), Q1.1 (G)
unnamed: IC1.2 (I), PAD11.1, R4.1
VCC: C15.1, IC1.5 (VCC), PAD2.1, R3.3 (E)

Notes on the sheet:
50V
0.5mm wire, 7 turns on 2mm aircore


Board: 2 copper layers, 75.0 x 60.0 mm, 28 parts (0 on the bottom side), 13 nets.

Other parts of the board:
U$4: LOGO_STASIS
U$5: LOGO_DKFZ

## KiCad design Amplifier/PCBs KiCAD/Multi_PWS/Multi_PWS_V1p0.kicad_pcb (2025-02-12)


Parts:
C1, C2, C3, C4: 22µF; PANASONIC_B
C5, C6: 10µF; C1210
C7, C8: 100nF; C1210
J1: 5V; 691210910008
J2: Fans (12V); 691210910008
J3: 8V; 691210910002
PAD1, PAD2, PAD3, PAD4, PAD5: SMD5; SMD2,54-5,08
U$1: LM2940IMPX-8.0; SOT223
U$2: LM2940IMPX-5.0; SOT223
X1: W237-3E

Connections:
5V: C3.+, C4.+, C8.1, J1.1, J1.2, J1.3, J1.4, U$2.3 (VCC)
8V: C1.+, C2.+, C7.1, J3.1, U$1.3 (VCC)
12V: C5.1, C6.1, J2.1, J2.2, J2.3, J2.4, PAD5.1, U$1.1 (IN), U$2.1 (IN)
GND: C1.-, C2.-, C3.-, C4.-, C5.2, C6.2, C7.2, C8.2, J1.5, J1.6, J1.7, J1.8, J2.5, J2.6, J2.7, J2.8, J3.2, PAD3.1, PAD4.1, U$1.2 (GND), U$1.4 (GND), U$2.2 (GND), U$2.4 (GND), X1.3
L: PAD1.1, X1.1
N: PAD2.1, X1.2

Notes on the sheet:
EEE-FN1C220R


Board: 2 copper layers, 140.0 x 120.0 mm, 29 parts (0 on the bottom side), 6 nets.

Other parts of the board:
@HOLE0, @HOLE1, @HOLE2, @HOLE3, @HOLE4, @HOLE5, @HOLE6, @HOLE7: (no value)
U$3: LOGO_DKFZ
U$4: LOGO_STASIS

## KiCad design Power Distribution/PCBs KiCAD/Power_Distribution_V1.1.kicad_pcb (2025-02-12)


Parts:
C1, C2, C4, C5, C6: 100µF; C1210
C3: 1µF; C1210
D1, D2, D3, D4, D5, D6, D7, D8: BAT54; SOT23
IC1, IC2, IC3, IC4, IC5, IC6, IC7, IC8: 741G14DBV; SOT23-5
J1: 5V_IN; 691210910002
J2, J3: DIG_IN; 691210910002
K1, K2, K3, K4, K5, K6, K7, K8: G2RE
LED1, LED2, LED3, LED4: LED3MM
Q1, Q2: 2A/20V/150mΩ; SOT26
R1, R2, R3, R4, R7, R8, R10, R11, R13: 47k; R0805
R5, R6, R9, R12: 180; R0805
R14, R15, R16, R17: 470; R0805
X1, X2, X3, X4, X5: W237-3E

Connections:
DIG_IN: D7.3 (C), J2.2, R7.1, R13.2
GND: C1.1, C2.1, C3.1, C4.1, C5.1, C6.1, D1.1 (A), D2.1 (A), D3.1 (A), D6.1 (A), IC1.3 (GND), IC2.3 (GND), IC3.3 (GND), IC4.3 (GND), IC5.3 (GND), IC6.3 (GND), IC7.3 (GND), IC8.3 (GND), J1.2, J2.1, J3.2, K1.2, K2.2, K3.2, K4.2, K5.2, K6.2, K7.2, K8.2, LED1.K (C), LED2.K (C), LED3.K (C), LED4.K (C), R13.1, X1.3, X2.3, X3.3, X4.3, X5.3
L: K2.P0 (P@1), K2.P1, K4.P0 (P@1), K4.P1, K6.P0 (P@1), K6.P1, K8.P0 (P@1), K8.P1, X1.1
N: K1.P0 (P@1), K1.P1, K3.P0 (P@1), K3.P1, K5.P0 (P@1), K5.P1, K7.P0 (P@1), K7.P1, X1.2
unnamed: K1.S0 (S), K1.S1 (S@1), X2.2
unnamed: K2.S0 (S), K2.S1 (S@1), X2.1
unnamed: K3.S0 (S), K3.S1 (S@1), X3.2
unnamed: K4.S0 (S), K4.S1 (S@1), X3.1
unnamed: K5.S0 (S), K5.S1 (S@1), X4.2
unnamed: K6.S0 (S), K6.S1 (S@1), X4.1
unnamed: IC1.4 (O), IC3.2 (I), Q2.G2 (G), R3.1
unnamed: IC2.4 (O), IC4.2 (I), Q1.G1 (G), R4.1
unnamed: C2.2, IC2.2 (I), R2.2, R16.2
unnamed: C1.2, IC1.2 (I), R1.2, R15.2
unnamed: D5.3 (C), IC3.4 (O), R2.1, R5.1
unnamed: LED2.A, R5.2
unnamed: D8.3 (C), IC4.4 (O), R6.1, R10.1
unnamed: LED3.A, R6.2
unnamed: K7.S0 (S), K7.S1 (S@1), X5.2
unnamed: K8.S0 (S), K8.S1 (S@1), X5.1
unnamed: IC5.4 (O), IC6.2 (I), Q2.G1 (G), R8.1
unnamed: C5.2, IC5.2 (I), R7.2, R14.2
unnamed: D4.3 (C), IC6.4 (O), R1.1, R9.1
unnamed: LED1.A, R9.2
unnamed: IC7.4 (O), IC8.2 (I), Q1.G2 (G), R11.1
unnamed: C6.2, IC7.2 (I), R10.2, R17.2
unnamed: IC8.4 (O), J3.1, R12.1
unnamed: LED4.A, R12.2
unnamed: D7.1 (A), R14.1
unnamed: D4.1 (A), R15.1
unnamed: D5.1 (A), R16.1
unnamed: D8.1 (A), R17.1
VCC: C3.2, C4.2, IC1.5 (VCC), IC2.5 (VCC), IC3.5 (VCC), IC4.5 (VCC), IC5.5 (VCC), IC6.5 (VCC), IC7.5 (VCC), IC8.5 (VCC), J1.1, Q1.S1 (S), Q1.S2 (S), Q2.S1 (S), Q2.S2 (S), R3.2, R4.2, R8.2, R11.2
VDELAY0: D1.3 (C), K1.1, K2.1, Q2.D1 (D)
VDELAY1: D2.3 (C), K3.1, K4.1, Q2.D2 (D)
VDELAY2: D3.3 (C), K5.1, K6.1, Q1.D1 (D)
VDELAY3: D6.3 (C), K7.1, K8.1, Q1.D2 (D)

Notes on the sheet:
Spray backside with protective paint after soldering~{}
1/2 DMP2240UDM
CON3
CON4
Con2
CON1


Board: 2 copper layers, 165.0 x 85.0 mm, 63 parts (0 on the bottom side), 37 nets.

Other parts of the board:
U$1: LOGO_STASIS
U$2: LOGO_DKFZ

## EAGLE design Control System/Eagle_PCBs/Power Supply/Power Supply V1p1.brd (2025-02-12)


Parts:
C1, C2, C3: 470µF; E5-10,5
LED1: LED5MM
PAD1: 5V; SMD2,54-5,08
PAD2, PAD5: GND; SMD2,54-5,08
PAD3: L; SMD2,54-5,08
PAD4: N; SMD2,54-5,08
R1: 330; R1206
X1: AK500/2-H
X2: AK500/3-H

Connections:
+5V: C1.+, C2.+, C3.+, PAD1.1, R1.2, X1.2
GND: C1.-, C2.-, C3.-, LED1.K (C), PAD2.1, PAD5.1, X1.1, X2.2
L: PAD3.1, X2.3
N: PAD4.1, X2.1
unnamed: LED1.A, R1.1

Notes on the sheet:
AKL 330-02
AKL 330-03


Board: 2 copper layers, 160.0 x 100.0 mm, 15 parts (0 on the bottom side), 5 nets.

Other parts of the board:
U$1: EK-FP
U$2: LOGO_STASIS
U$3: LOGO_DKFZ

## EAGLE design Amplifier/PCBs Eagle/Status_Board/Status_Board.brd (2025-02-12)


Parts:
270: R-EU_R0805; R0805
C1: 10nF; C0805
IC1, IC2, IC3: 74LVC1G17DBV; SOT23-5
IC4: 74LVC1G14DBV; SOT23-5
J1: 5V; 691210910002
J2: 75V_Status; 691210910002
J3: Amp_State; 691210910002
J4: UBL; 691210910002
LED1, LED2: LED5MM
LED3: DUOLED-RG-C; DUOLED-C-5MM
R2, R3: 220; R0805
R4: 180; R0805
R5, R6, R7: 47k; R0805

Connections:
GND: C1.2, IC1.3 (GND), IC2.3 (GND), IC3.3 (GND), IC4.3 (GND), J1.1, J2.1, J3.1, J4.1, LED1.K (C), LED2.K (C), LED3.C, R5.2, R6.1, R7.1
unnamed: IC4.4 (O), R4.1
unnamed: IC1.2 (I), J2.2, R5.1
unnamed: IC2.2 (I), IC4.2 (I), J3.2, R6.2
unnamed: IC3.2 (I), J4.2, R7.2
unnamed: 270.1, IC1.4 (O)
unnamed: IC2.4 (O), R2.1
unnamed: IC3.4 (O), R3.1
unnamed: 270.2, LED1.A
unnamed: LED3.AR, R2.2
unnamed: LED2.A, R3.2
unnamed: LED3.AX (AG), R4.2
VCC: C1.1, IC1.5 (VCC), IC2.5 (VCC), IC3.5 (VCC), IC4.5 (VCC), J1.2

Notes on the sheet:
TLUV5300
HLMP-3507-D0002
HLMP-D401


Board: 2 copper layers, 21.0 x 48.0 mm, 19 parts (0 on the bottom side), 13 nets.

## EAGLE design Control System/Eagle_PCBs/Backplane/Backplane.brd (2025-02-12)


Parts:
C1, C2, C3, C4, C5, C6, C7, C8, C9, C10, C11, C12, C13, C14, C15, C16, C17, C18: 10nF; C0603
X1, X2, X3, X4, X5, X6, X7, X8, X9, X10, X11, X12, X13, X14, X15, X16, X17, X18: FAC64S
X19: AKL320-2; MSTBV2

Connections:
5V: C1.2, C2.2, C3.2, C4.2, C5.2, C6.2, C7.2, C8.2, C9.2, C10.2, C11.2, C12.2, C13.2, C14.2, C15.2, C16.2, C17.2, C18.2, X1.A29, X1.A30, X1.A31, X1.A32, X2.A29, X2.A30, X2.A31, X2.A32, X3.A29, X3.A30, X3.A31, X3.A32, X4.A29, X4.A30, X4.A31, X4.A32, X5.A29, X5.A30, X5.A31, X5.A32, X6.A29, X6.A30, X6.A31, X6.A32, X7.A29, X7.A30, X7.A31, X7.A32, X8.A29, X8.A30, X8.A31, X8.A32, X9.A29, X9.A30, X9.A31, X9.A32, X10.A29, X10.A30, X10.A31, X10.A32, X11.A29, X11.A30, X11.A31, X11.A32, X12.A29, X12.A30, X12.A31, X12.A32, X13.A29, X13.A30, X13.A31, X13.A32, X14.A29, X14.A30, X14.A31, X14.A32, X15.A29, X15.A30, X15.A31, X15.A32, X16.A29, X16.A30, X16.A31, X16.A32, X17.A29, X17.A30, X17.A31, X17.A32, X18.A29, X18.A30, X18.A31, X18.A32, X19.1
A6: X1.A6, X2.A6, X3.A6, X4.A6, X5.A6, X6.A6, X7.A6, X8.A6, X9.A6, X10.A6, X11.A6, X12.A6, X13.A6, X14.A6, X15.A6, X16.A6, X17.A6, X18.A6
A7: X1.A7, X2.A7, X3.A7, X4.A7, X5.A7, X6.A7, X7.A7, X8.A7, X9.A7, X10.A7, X11.A7, X12.A7, X13.A7, X14.A7, X15.A7, X16.A7, X17.A7, X18.A7
A25: X1.A25, X2.A25, X3.A25, X4.A25, X5.A25, X6.A25, X7.A25, X8.A25, X9.A25, X10.A25, X11.A25, X12.A25, X13.A25, X14.A25, X15.A25, X16.A25, X17.A25, X18.A25
ADDR0: X1.C17, X2.C17, X3.C17, X4.C17, X5.C17, X6.C17, X7.C17, X8.C17, X9.C17, X10.C17, X11.C17, X12.C17, X13.C17, X14.C17, X15.C17, X16.C17, X17.C17, X18.C17
ADDR1: X1.C18, X2.C18, X3.C18, X4.C18, X5.C18, X6.C18, X7.C18, X8.C18, X9.C18, X10.C18, X11.C18, X12.C18, X13.C18, X14.C18, X15.C18, X16.C18, X17.C18, X18.C18
ADDR2: X1.C19, X2.C19, X3.C19, X4.C19, X5.C19, X6.C19, X7.C19, X8.C19, X9.C19, X10.C19, X11.C19, X12.C19, X13.C19, X14.C19, X15.C19, X16.C19, X17.C19, X18.C19
ADDR3: X1.C20, X2.C20, X3.C20, X4.C20, X5.C20, X6.C20, X7.C20, X8.C20, X9.C20, X10.C20, X11.C20, X12.C20, X13.C20, X14.C20, X15.C20, X16.C20, X17.C20, X18.C20
ADDR4: X1.C21, X2.C21, X3.C21, X4.C21, X5.C21, X6.C21, X7.C21, X8.C21, X9.C21, X10.C21, X11.C21, X12.C21, X13.C21, X14.C21, X15.C21, X16.C21, X17.C21, X18.C21
ADDR5: X1.C22, X2.C22, X3.C22, X4.C22, X5.C22, X6.C22, X7.C22, X8.C22, X9.C22, X10.C22, X11.C22, X12.C22, X13.C22, X14.C22, X15.C22, X16.C22, X17.C22, X18.C22
ADDR6: X1.C23, X2.C23, X3.C23, X4.C23, X5.C23, X6.C23, X7.C23, X8.C23, X9.C23, X10.C23, X11.C23, X12.C23, X13.C23, X14.C23, X15.C23, X16.C23, X17.C23, X18.C23
ADDR7: X1.C24, X2.C24, X3.C24, X4.C24, X5.C24, X6.C24, X7.C24, X8.C24, X9.C24, X10.C24, X11.C24, X12.C24, X13.C24, X14.C24, X15.C24, X16.C24, X17.C24, X18.C24
C31: X1.C31, X2.C31, X3.C31, X4.C31, X5.C31, X6.C31, X7.C31, X8.C31, X9.C31, X10.C31, X11.C31, X12.C31, X13.C31, X14.C31, X15.C31, X16.C31, X17.C31, X18.C31
CHIP0: X1.C25, X2.C25, X3.C25, X4.C25, X5.C25, X6.C25, X7.C25, X8.C25, X9.C25, X10.C25, X11.C25, X12.C25, X13.C25, X14.C25, X15.C25, X16.C25, X17.C25, X18.C25
CHIP1: X1.C26, X2.C26, X3.C26, X4.C26, X5.C26, X6.C26, X7.C26, X8.C26, X9.C26, X10.C26, X11.C26, X12.C26, X13.C26, X14.C26, X15.C26, X16.C26, X17.C26, X18.C26
CLK: X1.C29, X2.C29, X3.C29, X4.C29, X5.C29, X6.C29, X7.C29, X8.C29, X9.C29, X10.C29, X11.C29, X12.C29, X13.C29, X14.C29, X15.C29, X16.C29, X17.C29, X18.C29
DATA0: X1.C1, X2.C1, X3.C1, X4.C1, X5.C1, X6.C1, X7.C1, X8.C1, X9.C1, X10.C1, X11.C1, X12.C1, X13.C1, X14.C1, X15.C1, X16.C1, X17.C1, X18.C1
DATA1: X1.C2, X2.C2, X3.C2, X4.C2, X5.C2, X6.C2, X7.C2, X8.C2, X9.C2, X10.C2, X11.C2, X12.C2, X13.C2, X14.C2, X15.C2, X16.C2, X17.C2, X18.C2
DATA2: X1.C3, X2.C3, X3.C3, X4.C3, X5.C3, X6.C3, X7.C3, X8.C3, X9.C3, X10.C3, X11.C3, X12.C3, X13.C3, X14.C3, X15.C3, X16.C3, X17.C3, X18.C3
DATA3: X1.C4, X2.C4, X3.C4, X4.C4, X5.C4, X6.C4, X7.C4, X8.C4, X9.C4, X10.C4, X11.C4, X12.C4, X13.C4, X14.C4, X15.C4, X16.C4, X17.C4, X18.C4
DATA4: X1.C5, X2.C5, X3.C5, X4.C5, X5.C5, X6.C5, X7.C5, X8.C5, X9.C5, X10.C5, X11.C5, X12.C5, X13.C5, X14.C5, X15.C5, X16.C5, X17.C5, X18.C5
DATA5: X1.C6, X2.C6, X3.C6, X4.C6, X5.C6, X6.C6, X7.C6, X8.C6, X9.C6, X10.C6, X11.C6, X12.C6, X13.C6, X14.C6, X15.C6, X16.C6, X17.C6, X18.C6
DATA6: X1.C7, X2.C7, X3.C7, X4.C7, X5.C7, X6.C7, X7.C7, X8.C7, X9.C7, X10.C7, X11.C7, X12.C7, X13.C7, X14.C7, X15.C7, X16.C7, X17.C7, X18.C7
DATA7: X1.C8, X2.C8, X3.C8, X4.C8, X5.C8, X6.C8, X7.C8, X8.C8, X9.C8, X10.C8, X11.C8, X12.C8, X13.C8, X14.C8, X15.C8, X16.C8, X17.C8, X18.C8
DATA8: X1.C9, X2.C9, X3.C9, X4.C9, X5.C9, X6.C9, X7.C9, X8.C9, X9.C9, X10.C9, X11.C9, X12.C9, X13.C9, X14.C9, X15.C9, X16.C9, X17.C9, X18.C9
DATA9: X1.C10, X2.C10, X3.C10, X4.C10, X5.C10, X6.C10, X7.C10, X8.C10, X9.C10, X10.C10, X11.C10, X12.C10, X13.C10, X14.C10, X15.C10, X16.C10, X17.C10, X18.C10
DATA10: X1.C11, X2.C11, X3.C11, X4.C11, X5.C11, X6.C11, X7.C11, X8.C11, X9.C11, X10.C11, X11.C11, X12.C11, X13.C11, X14.C11, X15.C11, X16.C11, X17.C11, X18.C11
DATA11: X1.C12, X2.C12, X3.C12, X4.C12, X5.C12, X6.C12, X7.C12, X8.C12, X9.C12, X10.C12, X11.C12, X12.C12, X13.C12, X14.C12, X15.C12, X16.C12, X17.C12, X18.C12
DATA12: X1.C13, X2.C13, X3.C13, X4.C13, X5.C13, X6.C13, X7.C13, X8.C13, X9.C13, X10.C13, X11.C13, X12.C13, X13.C13, X14.C13, X15.C13, X16.C13, X17.C13, X18.C13
DATA13: X1.C14, X2.C14, X3.C14, X4.C14, X5.C14, X6.C14, X7.C14, X8.C14, X9.C14, X10.C14, X11.C14, X12.C14, X13.C14, X14.C14, X15.C14, X16.C14, X17.C14, X18.C14
DATA14: X1.C15, X2.C15, X3.C15, X4.C15, X5.C15, X6.C15, X7.C15, X8.C15, X9.C15, X10.C15, X11.C15, X12.C15, X13.C15, X14.C15, X15.C15, X16.C15, X17.C15, X18.C15
DATA15: X1.C16, X2.C16, X3.C16, X4.C16, X5.C16, X6.C16, X7.C16, X8.C16, X9.C16, X10.C16, X11.C16, X12.C16, X13.C16, X14.C16, X15.C16, X16.C16, X17.C16, X18.C16
ENABLE: X1.C32, X2.C32, X3.C32, X4.C32, X5.C32, X6.C32, X7.C32, X8.C32, X9.C32, X10.C32, X11.C32, X12.C32, X13.C32, X14.C32, X15.C32, X16.C32, X17.C32, X18.C32
EXT_MOD_CLK: X1.A26, X2.A26, X3.A26, X4.A26, X5.A26, X6.A26, X7.A26, X8.A26, X9.A26, X10.A26, X11.A26, X12.A26, X13.A26, X14.A26, X15.A26, X16.A26, X17.A26, X18.A26
GND: C1.1, C2.1, C3.1, C4.1, C5.1, C6.1, C7.1, C8.1, C9.1, C10.1, C11.1, C12.1, C13.1, C14.1, C15.1, C16.1, C17.1, C18.1, X1.A9, X1.A10, X1.A11, X1.A12, X1.A13, X1.A14, X1.A15, X1.A16, X1.A17, X1.A18, X1.A19, X1.A20, X1.A21, X1.A22, X1.A23, X1.A24, X2.A9, X2.A10, X2.A11, X2.A12, X2.A13, X2.A14, X2.A15, X2.A16, X2.A17, X2.A18, X2.A19, X2.A20, X2.A21, X2.A22, X2.A23, X2.A24, X3.A9, X3.A10, X3.A11, X3.A12, X3.A13, X3.A14, X3.A15, X3.A16, X3.A17, X3.A18, X3.A19, X3.A20, X3.A21, X3.A22, X3.A23, X3.A24, X4.A9, X4.A10, X4.A11, X4.A12, X4.A13, X4.A14, X4.A15, X4.A16, X4.A17, X4.A18, X4.A19, X4.A20, X4.A21, X4.A22, X4.A23, X4.A24, X5.A9, X5.A10, X5.A11, X5.A12, X5.A13, X5.A14, X5.A15, X5.A16, X5.A17, X5.A18, X5.A19, X5.A20, X5.A21, X5.A22, X5.A23, X5.A24, X6.A9, X6.A10, X6.A11, X6.A12, X6.A13, X6.A14, X6.A15, X6.A16, X6.A17, X6.A18, X6.A19, X6.A20, X6.A21, X6.A22, X6.A23, X6.A24, X7.A9, X7.A10, X7.A11, X7.A12, X7.A13, X7.A14, X7.A15, X7.A16, X7.A17, X7.A18, X7.A19, X7.A20, X7.A21, X7.A22, X7.A23, X7.A24, X8.A9, X8.A10, X8.A11, X8.A12, X8.A13, X8.A14, X8.A15, X8.A16, X8.A17, X8.A18, X8.A19, X8.A20, X8.A21, X8.A22, X8.A23, X8.A24, X9.A9, X9.A10, X9.A11, X9.A12, X9.A13, X9.A14, X9.A15, X9.A16, X9.A17, X9.A18, X9.A19, X9.A20, X9.A21, X9.A22, X9.A23, X9.A24, X10.A9, X10.A10, X10.A11, X10.A12, X10.A13, X10.A14, X10.A15, X10.A16, X10.A17, X10.A18, X10.A19, X10.A20, X10.A21, X10.A22, X10.A23, X10.A24, X11.A9, X11.A10, X11.A11, X11.A12, X11.A13, X11.A14, X11.A15, X11.A16, X11.A17, X11.A18, X11.A19, X11.A20, X11.A21, X11.A22, X11.A23, X11.A24, X12.A9, X12.A10, X12.A11, X12.A12, X12.A13, X12.A14, X12.A15, X12.A16, X12.A17, X12.A18, X12.A19, X12.A20, X12.A21, X12.A22, X12.A23, X12.A24, X13.A9, X13.A10, X13.A11, X13.A12, X13.A13, X13.A14, X13.A15, X13.A16, X13.A17, X13.A18, X13.A19, X13.A20, X13.A21, X13.A22, X13.A23, X13.A24, X14.A9, X14.A10, X14.A11, X14.A12, X14.A13, X14.A14, X14.A15, X14.A16, X14.A17, X14.A18, X14.A19, X14.A20, X14.A21, X14.A22, X14.A23, X14.A24, X15.A9, X15.A10, X15.A11, X15.A12, X15.A13, X15.A14, X15.A15, X15.A16, X15.A17, X15.A18, X15.A19, X15.A20, X15.A21, X15.A22, X15.A23, X15.A24, X16.A9, X16.A10, X16.A11, X16.A12, X16.A13, X16.A14, X16.A15, X16.A16, X16.A17, X16.A18, X16.A19, X16.A20, X16.A21, X16.A22, X16.A23, X16.A24, X17.A9, X17.A10, X17.A11, X17.A12, X17.A13, X17.A14, X17.A15, X17.A16, X17.A17, X17.A18, X17.A19, X17.A20, X17.A21, X17.A22, X17.A23, X17.A24, X18.A9, X18.A10, X18.A11, X18.A12, X18.A13, X18.A14, X18.A15, X18.A16, X18.A17, X18.A18, X18.A19, X18.A20, X18.A21, X18.A22, X18.A23, X18.A24, X19.2
MOD_CLK_TIMING: X1.A28, X2.A28, X3.A28, X4.A28, X5.A28, X6.A28, X7.A28, X8.A28, X9.A28, X10.A28, X11.A28, X12.A28, X13.A28, X14.A28, X15.A28, X16.A28, X17.A28, X18.A28
MOD_RESET: X1.A27, X2.A27, X3.A27, X4.A27, X5.A27, X6.A27, X7.A27, X8.A27, X9.A27, X10.A27, X11.A27, X12.A27, X13.A27, X14.A27, X15.A27, X16.A27, X17.A27, X18.A27
PICO: X1.A2, X2.A2, X3.A2, X4.A2, X5.A2, X6.A2, X7.A2, X8.A2, X9.A2, X10.A2, X11.A2, X12.A2, X13.A2, X14.A2, X15.A2, X16.A2, X17.A2, X18.A2
POCI: X1.A3, X2.A3, X3.A3, X4.A3, X5.A3, X6.A3, X7.A3, X8.A3, X9.A3, X10.A3, X11.A3, X12.A3, X13.A3, X14.A3, X15.A3, X16.A3, X17.A3, X18.A3
PROG: X1.C27, X2.C27, X3.C27, X4.C27, X5.C27, X6.C27, X7.C27, X8.C27, X9.C27, X10.C27, X11.C27, X12.C27, X13.C27, X14.C27, X15.C27, X16.C27, X17.C27, X18.C27
RES: X1.C28, X2.C28, X3.C28, X4.C28, X5.C28, X6.C28, X7.C28, X8.C28, X9.C28, X10.C28, X11.C28, X12.C28, X13.C28, X14.C28, X15.C28, X16.C28, X17.C28, X18.C28
SCLK: X1.A1, X2.A1, X3.A1, X4.A1, X5.A1, X6.A1, X7.A1, X8.A1, X9.A1, X10.A1, X11.A1, X12.A1, X13.A1, X14.A1, X15.A1, X16.A1, X17.A1, X18.A1
SPI_RESET: X1.A5, X2.A5, X3.A5, X4.A5, X5.A5, X6.A5, X7.A5, X8.A5, X9.A5, X10.A5, X11.A5, X12.A5, X13.A5, X14.A5, X15.A5, X16.A5, X17.A5, X18.A5
SS: X1.A4, X2.A4, X3.A4, X4.A4, X5.A4, X6.A4, X7.A4, X8.A4, X9.A4, X10.A4, X11.A4, X12.A4, X13.A4, X14.A4, X15.A4, X16.A4, X17.A4, X18.A4
UBL: X1.A8, X2.A8, X3.A8, X4.A8, X5.A8, X6.A8, X7.A8, X8.A8, X9.A8, X10.A8, X11.A8, X12.A8, X13.A8, X14.A8, X15.A8, X16.A8, X17.A8, X18.A8
WE: X1.C30, X2.C30, X3.C30, X4.C30, X5.C30, X6.C30, X7.C30, X8.C30, X9.C30, X10.C30, X11.C30, X12.C30, X13.C30, X14.C30, X15.C30, X16.C30, X17.C30, X18.C30



Board: 2 copper layers, 376.0 x 128.6 mm, 39 parts (19 on the bottom side), 46 nets.

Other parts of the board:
U$1: LOGO_STASIS
U$2: LOGO_DKFZ

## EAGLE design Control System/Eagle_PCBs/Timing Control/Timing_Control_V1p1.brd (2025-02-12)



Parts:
C11, C12: 10nF; C0603
D1, D2: BAT60J; SOD323_ST
IC1, IC3, IC9, IC10, IC17, IC18: SN74LV393ANSR; SO14
IC2: SN74LVC02AD; SO14
IC4, IC5, IC11, IC12, IC16, IC19, IC20: 74HC688DW; SO20W
IC6, IC13, IC21: 74LVC1G02DCK; SC70-5
IC7, IC14, IC22, IC29: 74AC16373; SSOP48DL
IC8, IC28, IC30, IC31, IC33, IC34, IC35, IC36, IC37, IC46: 74LVC1G08DCK; SC70-5
IC15, IC23, IC32, IC38: SN74LVC1G32DCKR; SC70-5
IC24, IC25: SN74LVCH16244ADLR; SSOP48DL
IC26: 74ALVC08; SO14
IC27: 74AHC04D-Q100J; SO14
IC39, IC45: 74LVC1G14DCK; SC70-5
IC40, IC44: 74LVC1G17DCK; SC70-5
J1: BUS; VG64P
JP1: 1/2 Clock; JP2
Q1: ECS-TXO-2520MV-100-AN-TR; 2.5X2.0_KXO-86-TCXO
R1, R3: 1k; R0603
R19, R20, R21, R22, R23, R24, R25, R26: 100k; R0603
S1: SWS008; SMS-008
U$1, U$2: 74LVC2G74DP,125; SSOP08
U$3: SMA_CON-H; BU-SMA-H

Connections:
5V: J1.A29, J1.A30, J1.A31, J1.A32; also elsewhere on the board
ADDR0: IC16.2 (P0), IC25.2 (1Y1)
ADDR1: IC16.4 (P1), IC25.3 (1Y2)
ADDR2: IC16.6 (P2), IC25.5 (1Y3)
ADDR3: IC16.8 (P3), IC25.6 (1Y4)
ADDR4: IC16.11 (P4), IC25.8 (2Y1)
ADDR5: IC16.13 (P5), IC25.9 (2Y2)
ADDR6: IC16.15 (P6), IC25.11 (2Y3)
ADDR7: IC16.17 (P7), IC25.12 (2Y4)
B1: IC4.3 (Q0), IC7.2 (1Q1)
B2: IC4.5 (Q1), IC7.3 (1Q2)
B3: IC4.7 (Q2), IC7.5 (1Q3)
B4: IC4.9 (Q3), IC7.6 (1Q4)
B5: IC4.12 (Q4), IC7.8 (1Q5)
B6: IC4.14 (Q5), IC7.9 (1Q6)
B7: IC4.16 (Q6), IC7.11 (1Q7)
B8: IC4.18 (Q7), IC7.12 (1Q8)
B9: IC5.3 (Q0), IC7.13 (2Q1)
B10: IC5.5 (Q1), IC7.14 (2Q2)
B11: IC5.7 (Q2), IC7.16 (2Q3)
B12: IC5.9 (Q3), IC7.17 (2Q4)
B13: IC5.12 (Q4), IC7.19 (2Q5)
B14: IC5.14 (Q5), IC7.20 (2Q6)
B15: IC5.16 (Q6), IC7.22 (2Q7)
B16: IC5.18 (Q7), IC7.23 (2Q8)
C1: IC19.3 (Q0), IC22.2 (1Q1)
C2: IC19.5 (Q1), IC22.3 (1Q2)
C3: IC19.7 (Q2), IC22.5 (1Q3)
C4: IC19.9 (Q3), IC22.6 (1Q4)
C5: IC19.12 (Q4), IC22.8 (1Q5)
C6: IC19.14 (Q5), IC22.9 (1Q6)
C7: IC19.16 (Q6), IC22.11 (1Q7)
C8: IC19.18 (Q7), IC22.12 (1Q8)
C9: IC20.3 (Q0), IC22.13 (2Q1)
C10: IC20.5 (Q1), IC22.14 (2Q2)
C11: IC20.7 (Q2), IC22.16 (2Q3)
C12: IC20.9 (Q3), IC22.17 (2Q4)
C13: IC20.12 (Q4), IC22.19 (2Q5)
C14: IC20.14 (Q5), IC22.20 (2Q6)
C15: IC20.16 (Q6), IC22.22 (2Q7)
C16: IC20.18 (Q7), IC22.23 (2Q8)
CHIP0: IC2.2 (I0), IC2.8 (I0), IC25.13 (3Y1), IC27.1 (I)
CHIP1: IC2.3 (I1), IC2.6 (I1), IC25.14 (3Y2), IC27.3 (I)
CLK: IC1.1 (A), JP1.2
CLK_C: IC17.1 (A), IC30.4 (O)
CLK_D: IC9.1 (A), IC31.4 (O)
CLR1: IC9.2 (CLR), IC9.12 (CLR), IC10.2 (CLR), IC10.12 (CLR), IC15.4 (O)
CLR2: IC17.2 (CLR), IC17.12 (CLR), IC18.2 (CLR), IC18.12 (CLR), IC23.4 (O)
CONT_MODE: IC29.2 (1Q1), IC32.2 (I1); also elsewhere on the board
D1: IC11.3 (Q0), IC14.2 (1Q1)
D2: IC11.5 (Q1), IC14.3 (1Q2)
D3: IC11.7 (Q2), IC14.5 (1Q3)
D4: IC11.9 (Q3), IC14.6 (1Q4)
D5: IC11.12 (Q4), IC14.8 (1Q5)
D6: IC11.14 (Q5), IC14.9 (1Q6)
D7: IC11.16 (Q6), IC14.11 (1Q7)
D8: IC11.18 (Q7), IC14.12 (1Q8)
D9: IC12.3 (Q0), IC14.13 (2Q1)
D10: IC12.5 (Q1), IC14.14 (2Q2)
D11: IC12.7 (Q2), IC14.16 (2Q3)
D12: IC12.9 (Q3), IC14.17 (2Q4)
D13: IC12.12 (Q4), IC14.19 (2Q5)
D14: IC12.14 (Q5), IC14.20 (2Q6)
D15: IC12.16 (Q6), IC14.22 (2Q7)
D16: IC12.18 (Q7), IC14.23 (2Q8)
DATA0: IC7.47 (1D1), IC14.47 (1D1), IC22.47 (1D1), IC24.2 (1Y1), IC29.47 (1D1)
DATA1: IC7.46 (1D2), IC14.46 (1D2), IC22.46 (1D2), IC24.3 (1Y2), IC29.46 (1D2)
DATA2: IC7.44 (1D3), IC14.44 (1D3), IC22.44 (1D3), IC24.5 (1Y3), IC37.1 (I0)
DATA3: IC7.43 (1D4), IC14.43 (1D4), IC22.43 (1D4), IC24.6 (1Y4), IC29.43 (1D4)
DATA4: IC7.41 (1D5), IC14.41 (1D5), IC22.41 (1D5), IC24.8 (2Y1), IC29.41 (1D5)
DATA5: IC7.40 (1D6), IC14.40 (1D6), IC22.40 (1D6), IC24.9 (2Y2), IC29.40 (1D6)
DATA6: IC7.38 (1D7), IC14.38 (1D7), IC22.38 (1D7), IC24.11 (2Y3), IC29.38 (1D7)
DATA7: IC7.37 (1D8), IC14.37 (1D8), IC22.37 (1D8), IC24.12 (2Y4), IC29.37 (1D8)
DATA8: IC7.36 (2D1), IC14.36 (2D1), IC22.36 (2D1), IC24.13 (3Y1), IC29.36 (2D1)
DATA9: IC7.35 (2D2), IC14.35 (2D2), IC22.35 (2D2), IC24.14 (3Y2), IC29.35 (2D2)
DATA10: IC7.33 (2D3), IC14.33 (2D3), IC22.33 (2D3), IC24.16 (3Y3), IC29.33 (2D3)
DATA11: IC7.32 (2D4), IC14.32 (2D4), IC22.32 (2D4), IC24.17 (3Y4), IC29.32 (2D4)
DATA12: IC7.30 (2D5), IC14.30 (2D5), IC22.30 (2D5), IC24.19 (4Y1), IC29.30 (2D5)
DATA13: IC7.29 (2D6), IC14.29 (2D6), IC22.29 (2D6), IC24.20 (4Y2), IC29.29 (2D6)
DATA14: IC7.27 (2D7), IC14.27 (2D7), IC22.27 (2D7), IC24.22 (4Y3), IC29.27 (2D7)
DATA15: IC7.26 (2D8), IC14.26 (2D8), IC22.26 (2D8), IC24.23 (4Y4), IC29.26 (2D8)
ENABLE: IC25.23 (4Y4), IC46.1 (I0)
GND: C11.2, C12.2, IC1.7 (GND), IC2.7 (GND), IC3.7 (GND), IC4.1 (G), IC4.10 (GND), IC5.1 (G), IC5.10 (GND), IC6.3 (GND), IC7.1 (1OE), IC7.4 (GND), IC7.10 (GND), IC7.15 (GND), IC7.21 (GND), IC7.24 (2OE), IC7.28 (GND), IC7.34 (GND), IC7.39 (GND), IC7.45 (GND), IC8.3 (GND), IC9.7 (GND), IC10.7 (GND), IC11.1 (G), IC11.10 (GND), IC12.1 (G), IC12.10 (GND), IC13.3 (GND), IC14.1 (1OE), IC14.4 (GND), IC14.10 (GND), IC14.15 (GND), IC14.21 (GND), IC14.24 (2OE), IC14.28 (GND), IC14.34 (GND), IC14.39 (GND), IC14.45 (GND), IC15.3 (GND), IC16.1 (G), IC16.10 (GND), IC17.7 (GND), IC18.7 (GND), IC19.1 (G), IC19.10 (GND), IC20.1 (G), IC20.10 (GND), IC21.3 (GND), IC22.1 (1OE), IC22.4 (GND), IC22.10 (GND), IC22.15 (GND), IC22.21 (GND), IC22.24 (2OE), IC22.28 (GND), IC22.34 (GND), IC22.39 (GND), IC22.45 (GND), IC23.3 (GND), IC24.1 (1G), IC24.4 (GND), IC24.10 (GND), IC24.15 (GND), IC24.21 (GND), IC24.24 (4G), IC24.25 (3G), IC24.28 (GND), IC24.34 (GND), IC24.39 (GND), IC24.45 (GND), IC24.48 (2G), IC25.1 (1G), IC25.4 (GND), IC25.10 (GND), IC25.15 (GND), IC25.21 (GND), IC25.24 (4G), IC25.25 (3G), IC25.28 (GND), IC25.34 (GND), IC25.39 (GND), IC25.45 (GND), IC25.48 (2G), IC26.7 (GND), IC27.7 (GND), IC28.3 (GND), IC29.1 (1OE), IC29.4 (GND), IC29.10 (GND), IC29.15 (GND), IC29.21 (GND), IC29.24 (2OE), IC29.28 (GND), IC29.34 (GND), IC29.39 (GND), IC29.45 (GND), IC30.3 (GND), IC31.3 (GND), IC32.3 (GND), IC33.3 (GND), IC34.3 (GND), IC35.3 (GND), IC36.3 (GND), IC37.3 (GND), IC38.3 (GND), IC39.3 (GND), IC40.3 (GND), IC44.3 (GND), IC45.3 (GND), IC46.3 (GND), J1.A9, J1.A10, J1.A11, J1.A12, J1.A13, J1.A14, J1.A15, J1.A16, J1.A17, J1.A18, J1.A19, J1.A20, J1.A21, J1.A22, J1.A23, J1.A24, Q1.2 (GND), R19.1, R20.1, R21.1, R22.1, R23.1, R24.1, R25.1, R26.1, U$1.1 (CLK), U$1.2 (D), U$1.4 (GND), U$2.4 (GND), U$3.2 (GND), U$3.3 (GND), U$3.4 (GND), U$3.5 (GND); also elsewhere on the board
GND/NC: Q1.1 (GND/NC)
IS_EQUAL_B: IC1.2 (CLR), IC1.12 (CLR), IC3.2 (CLR), IC3.12 (CLR), IC6.4 (O), IC8.1 (I0), IC45.2 (I)
IS_EQUAL_C: IC21.4 (O), IC23.2 (I1), IC27.11 (I), IC33.1 (I0)
IS_EQUAL_D: IC13.4 (O), IC15.2 (I1), IC27.9 (I)
IS_SEL: IC27.6 (O), IC28.2 (I1); also elsewhere on the board
MOD_CLK_TIMING: IC8.4 (O), J1.A28
MOD_RESET: IC33.4 (O), J1.A27
MOD_RES_SEL: IC29.3 (1Q2), IC33.2 (I1)
unnamed: IC1.6 (QD), IC1.13 (A), IC4.8 (P3)
unnamed: IC1.8 (QD), IC3.1 (A), IC4.17 (P7)
unnamed: IC3.6 (QD), IC3.13 (A), IC5.8 (P3)
unnamed: IC8.2 (I1), IC35.4 (O)
unnamed: IC1.3 (QA), IC4.2 (P0)
unnamed: IC1.4 (QB), IC4.4 (P1)
unnamed: IC1.5 (QC), IC4.6 (P2)
unnamed: IC1.11 (QA), IC4.11 (P4)
unnamed: IC1.10 (QB), IC4.13 (P5)
unnamed: IC1.9 (QC), IC4.15 (P6)
unnamed: IC3.3 (QA), IC5.2 (P0)
unnamed: IC3.4 (QB), IC5.4 (P1)
unnamed: IC3.5 (QC), IC5.6 (P2)
unnamed: IC9.6 (QD), IC9.13 (A), IC11.8 (P3)
unnamed: IC3.11 (QA), IC5.11 (P4)
unnamed: IC3.10 (QB), IC5.13 (P5)
unnamed: IC3.9 (QC), IC5.15 (P6)
unnamed: IC3.8 (QD), IC5.17 (P7)
unnamed: IC4.19 (P=Q), IC6.1 (I0)
unnamed: IC5.19 (P=Q), IC6.2 (I1)
unnamed: IC9.8 (QD), IC10.1 (A), IC11.17 (P7)
unnamed: IC10.6 (QD), IC10.13 (A), IC12.8 (P3)
unnamed: IC9.3 (QA), IC11.2 (P0)
unnamed: IC9.4 (QB), IC11.4 (P1)
unnamed: IC9.5 (QC), IC11.6 (P2)
unnamed: IC9.11 (QA), IC11.11 (P4)
unnamed: IC9.10 (QB), IC11.13 (P5)
unnamed: IC9.9 (QC), IC11.15 (P6)
unnamed: IC10.3 (QA), IC12.2 (P0)
unnamed: IC10.4 (QB), IC12.4 (P1)
unnamed: IC10.5 (QC), IC12.6 (P2)
unnamed: IC10.11 (QA), IC12.11 (P4)
unnamed: IC10.10 (QB), IC12.13 (P5)
unnamed: IC10.9 (QC), IC12.15 (P6)
unnamed: IC10.8 (QD), IC12.17 (P7)
unnamed: IC11.19 (P=Q), IC13.1 (I0)
unnamed: IC12.19 (P=Q), IC13.2 (I1)
unnamed: IC27.12 (O), IC34.2 (I1)
unnamed: IC17.6 (QD), IC17.13 (A), IC19.8 (P3)
unnamed: IC16.3 (Q0), R19.2, S1.16
unnamed: IC17.8 (QD), IC18.1 (A), IC19.17 (P7)
unnamed: IC18.6 (QD), IC18.13 (A), IC20.8 (P3)
unnamed: IC17.3 (QA), IC19.2 (P0)
unnamed: IC17.4 (QB), IC19.4 (P1)
unnamed: IC17.5 (QC), IC19.6 (P2)
unnamed: IC17.11 (QA), IC19.11 (P4)
unnamed: IC17.10 (QB), IC19.13 (P5)
unnamed: IC17.9 (QC), IC19.15 (P6)
unnamed: IC18.3 (QA), IC20.2 (P0)
unnamed: IC18.4 (QB), IC20.4 (P1)
unnamed: IC18.5 (QC), IC20.6 (P2)
unnamed: IC18.11 (QA), IC20.11 (P4)
unnamed: IC18.10 (QB), IC20.13 (P5)
unnamed: IC18.9 (QC), IC20.15 (P6)
unnamed: IC18.8 (QD), IC20.17 (P7)
unnamed: IC19.19 (P=Q), IC21.1 (I0)
unnamed: IC20.19 (P=Q), IC21.2 (I1)
unnamed: IC34.4 (O), IC36.2 (I1)
unnamed: IC24.47 (1A1), J1.C1
unnamed: IC24.46 (1A2), J1.C2
unnamed: IC24.44 (1A3), J1.C3
unnamed: IC24.43 (1A4), J1.C4
unnamed: IC24.41 (2A1), J1.C5
unnamed: IC16.5 (Q1), R20.2, S1.15
unnamed: IC16.7 (Q2), R21.2, S1.14
unnamed: IC16.9 (Q3), R22.2, S1.13
unnamed: IC16.12 (Q4), R23.2, S1.12
unnamed: IC16.14 (Q5), R24.2, S1.11
unnamed: IC16.16 (Q6), R25.2, S1.10
unnamed: IC16.18 (Q7), R26.2, S1.9
unnamed: IC24.40 (2A2), J1.C6
unnamed: IC24.38 (2A3), J1.C7
unnamed: IC24.37 (2A4), J1.C8
unnamed: IC24.36 (3A1), J1.C9
unnamed: IC24.35 (3A2), J1.C10
unnamed: IC24.33 (3A3), J1.C11
unnamed: IC24.32 (3A4), J1.C12
unnamed: IC24.30 (4A1), J1.C13
unnamed: IC24.29 (4A2), J1.C14
unnamed: IC16.19 (P=Q), IC27.5 (I)
unnamed: IC24.27 (4A3), J1.C15
unnamed: IC24.26 (4A4), J1.C16
unnamed: IC25.47 (1A1), J1.C17
unnamed: IC25.46 (1A2), J1.C18
unnamed: IC25.44 (1A3), J1.C19
unnamed: IC25.43 (1A4), J1.C20
unnamed: IC25.41 (2A1), J1.C21
unnamed: IC25.40 (2A2), J1.C22
unnamed: IC25.38 (2A3), J1.C23
unnamed: IC25.37 (2A4), J1.C24
unnamed: IC25.36 (3A1), J1.C25
unnamed: IC25.35 (3A2), J1.C26
unnamed: IC25.33 (3A3), J1.C27
unnamed: IC25.32 (3A4), J1.C28
unnamed: IC25.30 (4A1), J1.C29
unnamed: IC25.29 (4A2), J1.C30
unnamed: IC25.27 (4A3), J1.C31
unnamed: IC25.26 (4A4), J1.C32
unnamed: IC2.5 (I0), IC2.11 (I0), IC27.2 (O)
unnamed: IC2.9 (I1), IC2.12 (I1), IC27.4 (O)
unnamed: IC2.1 (O), IC26.2 (I1)
unnamed: IC2.4 (O), IC26.5 (I1)
unnamed: IC2.10 (O), IC26.10 (I1)
unnamed: IC2.13 (O), IC26.13 (I1)
unnamed: IC26.1 (I0), IC26.4 (I0), IC26.9 (I0), IC26.12 (I0), IC28.4 (O)
unnamed: IC30.2 (I1), IC32.1 (I0), U$1.5 (Q)
unnamed: IC31.2 (I1), U$1.3 (!Q)
unnamed: IC27.8 (O), U$1.7 (!S)
unnamed: IC27.10 (O), U$1.6 (!R)
unnamed: IC32.4 (O), IC36.1 (I0)
unnamed: JP1.1, Q1.3 (OUT), U$2.1 (CLK)
unnamed: IC29.44 (1D3), IC37.4 (O)
unnamed: U$2.2 (D), U$2.3 (!Q)
unnamed: JP1.3, U$2.5 (Q)
unnamed: IC29.25 (2C), IC29.48 (1C), IC38.4 (O)
unnamed: IC37.2 (I1), IC40.4 (O)
unnamed: C11.1, D1.A, IC40.2 (I), R3.2
unnamed: IC38.1 (I0), IC39.4 (O)
unnamed: C12.1, D2.A, IC39.2 (I), R1.2
unnamed: IC34.1 (I0), IC46.4 (O)
unnamed: IC44.4 (O), U$3.1
unnamed: IC30.1 (I0), IC31.1 (I0), IC45.4 (O)
PROG: IC25.16 (3Y3), IC27.13 (I)
RES: IC15.1 (I0), IC23.1 (I0), IC25.17 (3Y4)
TRIG_ENBL: IC29.6 (1Q4), IC35.1 (I0)
TX: IC35.2 (I1), IC36.4 (O), IC44.2 (I), J1.A8; also elsewhere on the board
UBL_ENBL: IC29.5 (1Q3), IC46.2 (I1)
VCC: D1.C, D2.C, IC1.14 (VCC), IC2.14 (VCC), IC3.14 (VCC), IC4.20 (VCC), IC5.20 (VCC), IC6.5 (VCC), IC7.7 (VCC), IC7.18 (VCC), IC7.31 (VCC), IC7.42 (VCC), IC8.5 (VCC), IC9.14 (VCC), IC10.14 (VCC), IC11.20 (VCC), IC12.20 (VCC), IC13.5 (VCC), IC14.7 (VCC), IC14.18 (VCC), IC14.31 (VCC), IC14.42 (VCC), IC15.5 (VCC), IC16.20 (VCC), IC17.14 (VCC), IC18.14 (VCC), IC19.20 (VCC), IC20.20 (VCC), IC21.5 (VCC), IC22.7 (VCC), IC22.18 (VCC), IC22.31 (VCC), IC22.42 (VCC), IC23.5 (VCC), IC24.7 (VCC), IC24.18 (VCC), IC24.31 (VCC), IC24.42 (VCC), IC25.7 (VCC), IC25.18 (VCC), IC25.31 (VCC), IC25.42 (VCC), IC26.14 (VCC), IC27.14 (VCC), IC28.5 (VCC), IC29.7 (VCC), IC29.18 (VCC), IC29.31 (VCC), IC29.42 (VCC), IC30.5 (VCC), IC31.5 (VCC), IC32.5 (VCC), IC33.5 (VCC), IC34.5 (VCC), IC35.5 (VCC), IC36.5 (VCC), IC37.5 (VCC), IC38.5 (VCC), IC39.5 (VCC), IC40.5 (VCC), IC44.5 (VCC), IC45.5 (VCC), IC46.5 (VCC), Q1.4 (VDD), R1.1, R3.1, S1.1, S1.2, S1.3, S1.4, S1.5, S1.6, S1.7, S1.8, U$1.8 (VCC), U$2.6 (!R), U$2.7 (!S), U$2.8 (VCC); also elsewhere on the board
WE: IC25.20 (4Y2), IC28.1 (I0)
W_A: IC26.3 (O), IC38.2 (I1)
W_B: IC7.25 (2C), IC7.48 (1C), IC26.6 (O)
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

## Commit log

2025-02-12 Upload Array data and Main Documentation Document.
    [Decoupling_Board.brd, Decoupling_Board.kicad_pcb, Decoupling_Board.kicad_sch, Decoupling_Board.sch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]
2025-02-12 Upload PCBs and Housing
    [24V_PWS.brd, 24V_PWS.kicad_pcb, 24V_PWS.kicad_sch, 24V_PWS.sch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]
2025-02-12 Added Spice Simulations
    -HPA
    -2nd stage amplifier
    -Voltage Control
2025-03-19 Updated Calibration Changed the way the calibration should be done and changed the documentation accordingly.
2025-09-16 Added Fusion360 file for array housing
    [Coil housing 2 v2.f3d]
2025-09-16 Added Partlist
    Added partlist with prices at time of purchase.
    [Part List STASIS Electronics.xlsx]

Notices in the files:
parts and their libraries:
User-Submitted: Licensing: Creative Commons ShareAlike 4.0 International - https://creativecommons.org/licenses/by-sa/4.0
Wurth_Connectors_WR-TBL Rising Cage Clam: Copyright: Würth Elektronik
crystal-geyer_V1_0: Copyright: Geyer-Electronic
